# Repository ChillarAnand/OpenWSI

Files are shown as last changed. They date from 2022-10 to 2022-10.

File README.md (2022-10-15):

### OpenWSI

OpenWSI: a low-cost, high-throughput whole slide imaging system via single-frame autofocusing and open-source hardware

### Description

Recent advancements in whole slide imaging (WSI) have moved pathology closer to digital practice. Existing systems require precise mechanical control and the cost is prohibitive for most individual pathologists. Here we report a low-cost and high-throughput WSI system termed OpenWSI. The reported system is built using off-the-shelf components including a programmable LED array, a photographic lens, and a low-cost computer numerical control (CNC) router. Different from conventional WSI platforms, our system performs real-time single-frame autofocusing using color-multiplexed illumination. For axial positioning control, we perform coarse adjustment using the CNC router and precise adjustment using the ultrasonic motor ring in the photographic lens. By using a 20X objective lens, we show that the OpenWSI system has a resolution of ~0.7 microns. It can acquire whole slide images of a 225-mm^2 region in ~2 mins, with throughput comparable to existing high-end platforms. The reported system offers a turnkey solution to transform the high-end WSI platforms into one that can be made broadly available and utilizable without loss of capacity.

### Source

https://arxiv.org/abs/1912.03446

### Notes

This repo contains resources mentioned in the above paper. This repo is meant for collaboration for implementation.

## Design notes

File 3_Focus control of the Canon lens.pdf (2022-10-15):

## Focus control of Canon lenses

Chengfei Guo, Zichao Bian, Shaowei Jiang, and Guoan Zheng Department of Biomedical Engineering, University of Connecticut, Storrs, Connecticut 06269, USA

Step 1: Tools Preparation [1]
Below are the tools for lens modification.

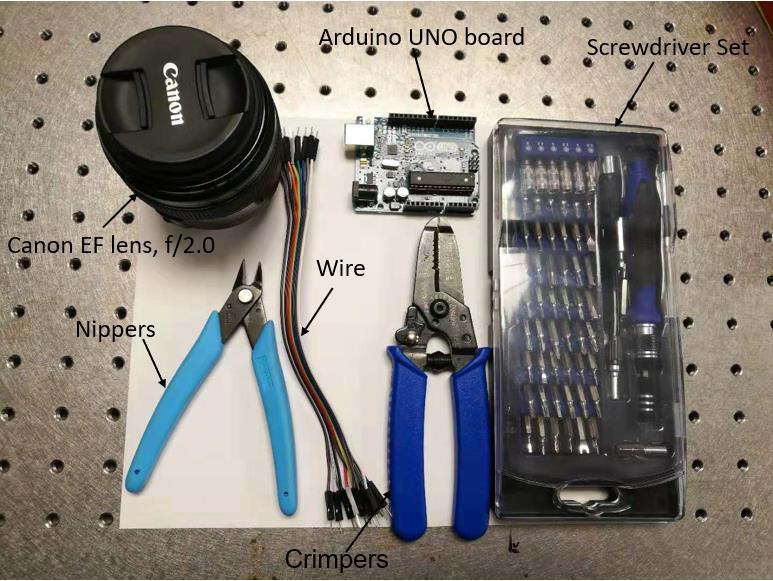
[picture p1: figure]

Figure 1: Tools preparation.

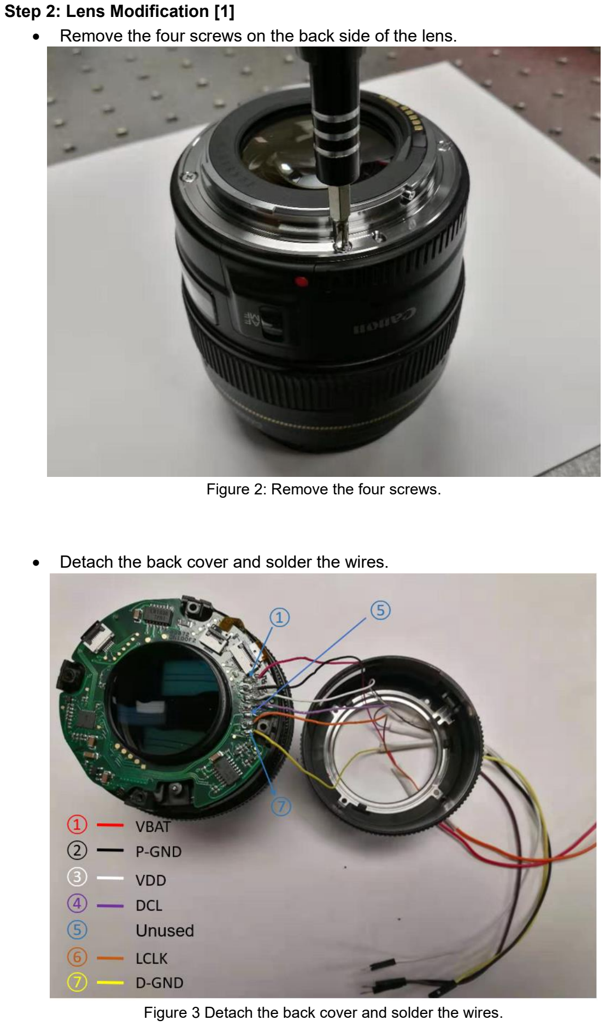
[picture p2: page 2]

Step 2: Lens Modification [1]
- Remove the four screws on the back side of the lens.

Figure 2: Remove the four screws.

- Detach the back cover and solder the wires.

Figure 3 Detach the back cover and solder the wires.

- Reassemble

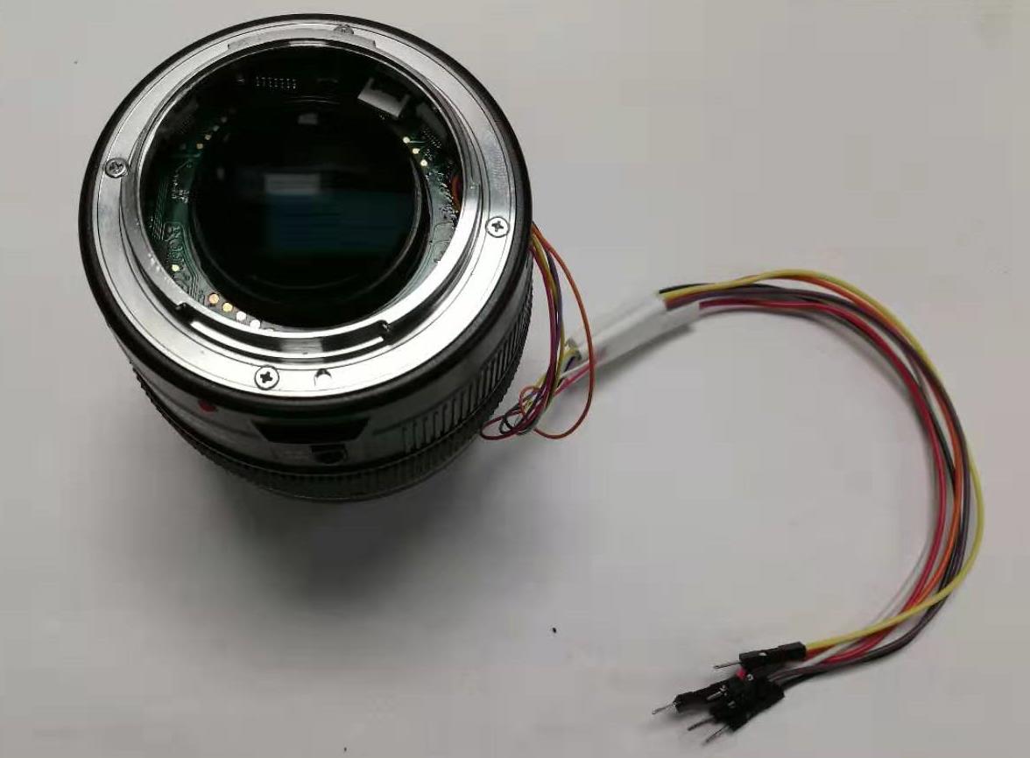
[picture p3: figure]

Figure 4: Reassemble the lens parts.

Step 3: Wire Connection [1]
The lens has motors and control circuits inside and can be connected to an external board via a 7-pin connector. Three pins for the power supply and four pins for a standard SPI interface. We need to wire the pins from outside so that we can send commands from an external board to move the lens ring to the in-focus position. We use an Arduino Uno board (ATmega328P) to perform focus control.
Pin 11 below is defined to send the ‘moving’ command and is connected to the DCL pin of the lens. Pin 13 is used for transferring the clock, which is connected to the CLK pin on the lens. Two GND pins are connected to the D-GND pin and P-GND pin on the lens, respectively. One 5V pin gives power supply for the lens control circuits and is connected to the VDD pin on the lens. We define an output pin as the digital logic high for the power supply of lens motors. The pinout diagram and schematic is listed below.

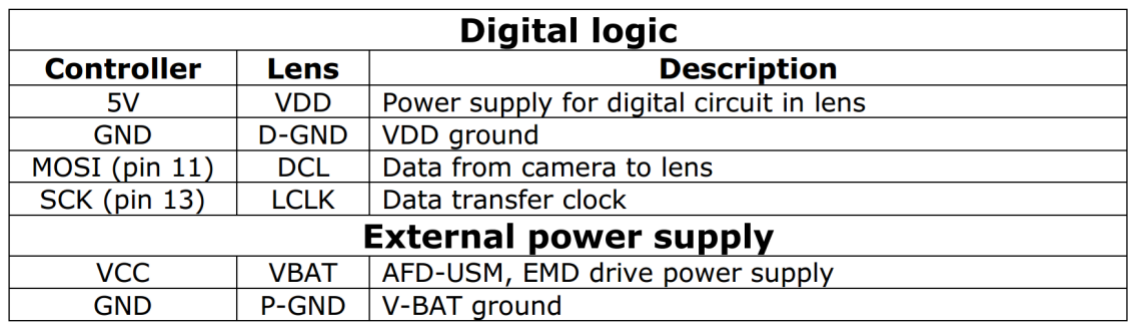
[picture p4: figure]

Figure 5: Pinout diagram.

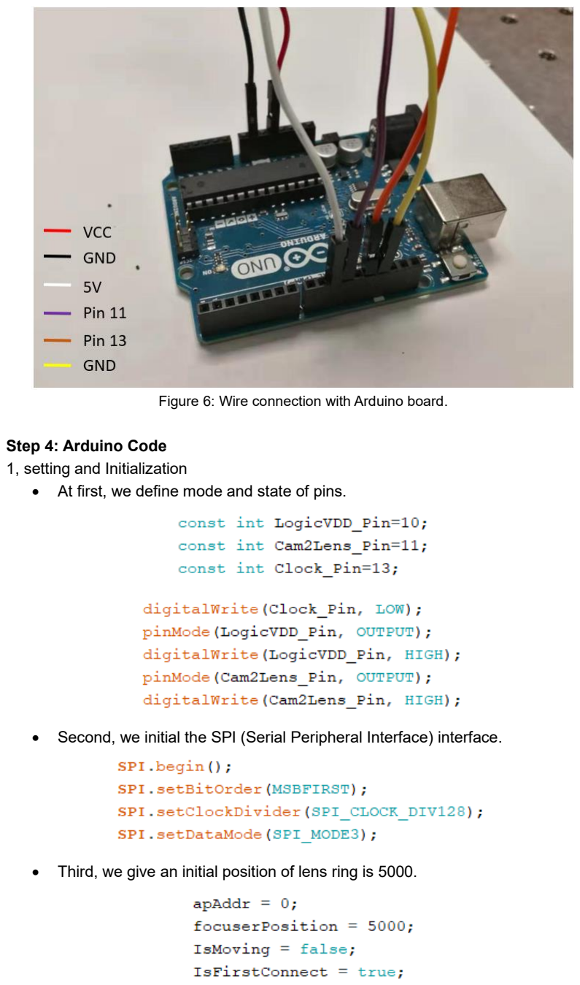
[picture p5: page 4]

Figure 6: Wire connection with Arduino board.

Step 4: Arduino Code
1, setting and Initialization
- At first, we define mode and state of pins.
- Second, we initial the SPI (Serial Peripheral Interface) interface.
- Third, we give an initial position of lens ring is 5000.

- Next, we set the baud rate to 2000000.
- Finally, we initialize the lens.

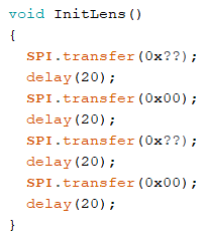
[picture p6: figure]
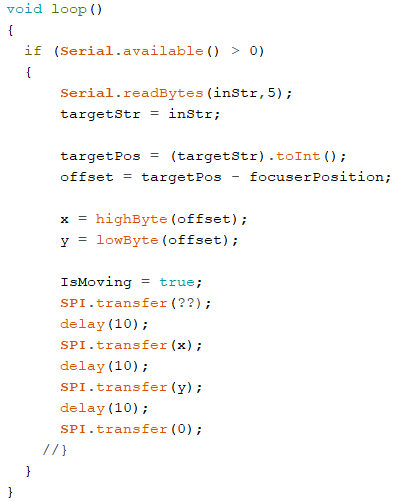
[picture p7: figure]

Note: For the commands of ??, one can email guochengfeii@gmail.com Reference
[1] http://web.media.mit.edu/~bandy/invariant/move_lens.pdf

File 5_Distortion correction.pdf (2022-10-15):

# Digital distortion correction in OpenWSI

We correct the distortion by the following steps:

First, we use a known binary hole-array mask as the sample and capture the corresponding brightfield image in Fig. 1.

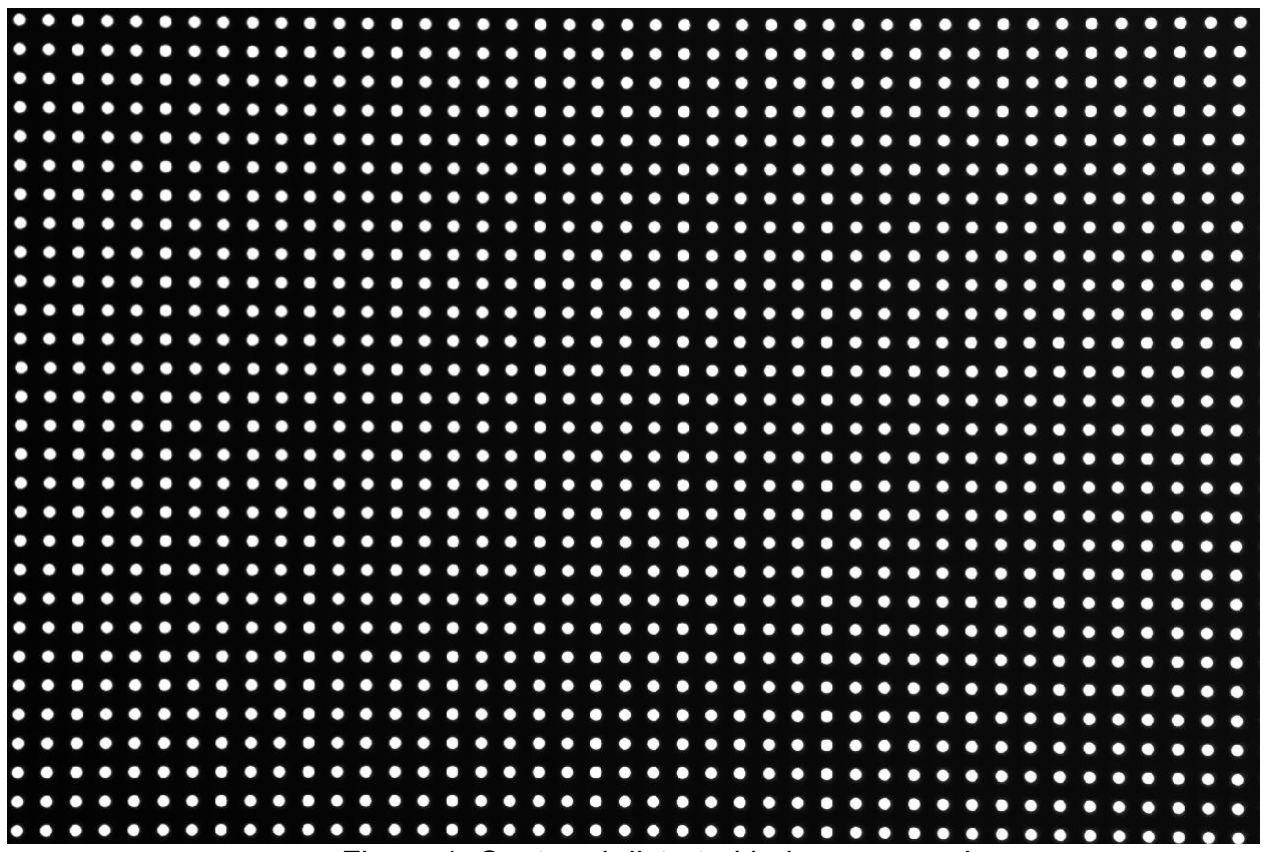
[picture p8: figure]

Figure 1: Captured distorted hole-array mask.

Second, we match the central holes with that of the ground-truth mask. At the edge of the captured hole array image, we can see the position mismatch between the ground-truth mask and the captured image, as shown in Fig. 2(a).

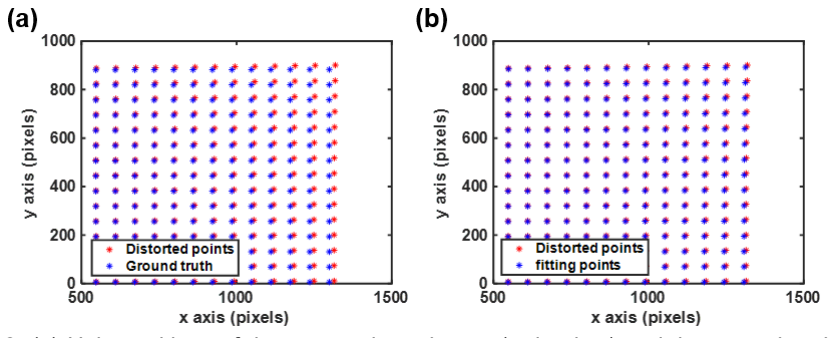
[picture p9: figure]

Figure 2: (a) Hole positions of the captured raw image (red points) and the ground-truth mask (blue points). (b) Hole positions of the captured image after the fitting process.

Third, we fit the distorted hole-positions using those of ground-truth hole positions:

xdistort = x(1 + k1

(x

2 + y

2
) + k2(x

2 + y

2
)

2
)

ydistort = y(1 + k1

(x

2 + y

2
) + k2(x

2 + y

2
)

2
)

where x and y are the ground-truth pairs, xdistort and ydistort are the distorted pairs, k1 and k2 are the coefficients for calibration. In Fig. 2(b), we can see that the fitted hole positions are well aligned with the positions of the ground truth mask.

Fourth, we apply the coefficients to correct the distortion of the raw captured images. We correct the distortion of all tiles we captured. For each image, the processing time is ~0.13 seconds. In Fig. 3, we show the stitching performance with and without the reported distortion correction process. We can see that there are no stitching artifacts after performing distortion correction. The demo code can be found in ‘Demo code’.

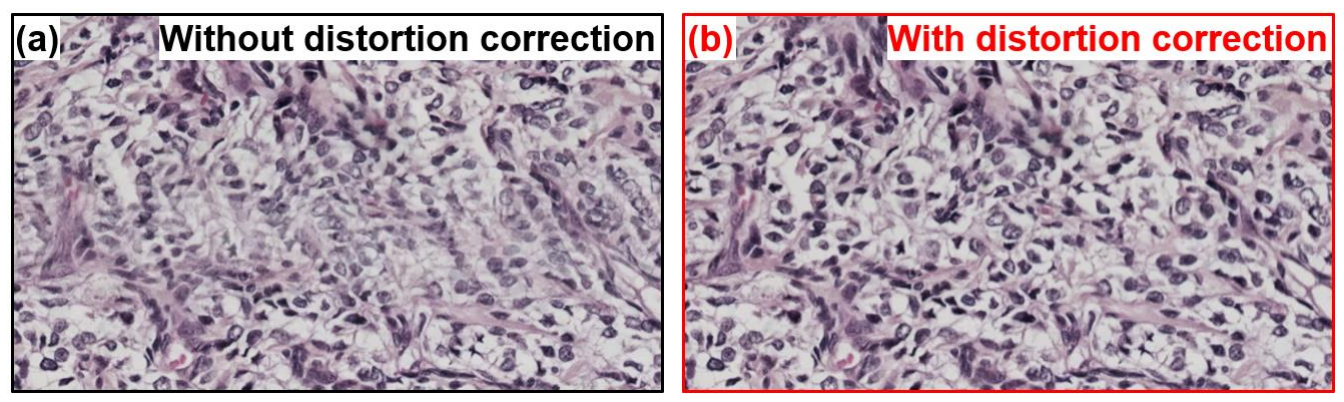
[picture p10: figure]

Fig. 3. Stitching performance without (a) and with (b) distortion correction.

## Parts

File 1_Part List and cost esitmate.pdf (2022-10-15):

## Table 1 Part list and estimated cost for the OpenWSI system

| Item | Specification | Amount | Cost (Unit) | Company
Standard Part | Aluminum Breadboard | MB12 12" x 12" x 1/2" | 1 | $151.0 | Thorlabs
| Optical Posts | TR2 Ø1/2", L = 2" | 5 | $5.19 | Thorlabs
| Post Holders | UPH2 Ø1/2", L = 2" | 1 | $32.04 | Thorlabs
| Lens Tube Slip Rings | SM2RC Ø2.20" | 1 | $30.99 | Thorlabs
| Kinematic Mount | KC1-T | 1 | $97.45 | Thorlabs
| Microscope Slide Clips | SLH1 | 1 | $44.39 | Thorlabs
| Camera | DFK 33UX183 | 1 | $675.0 | The Imaging Source
| Camera Lens | Canon EF -100mm - f/2.0 | 1 | $499.0 | Amazon
| Base | MYSWEETY DIY CNC Engraving Machine | 1 | $169.89 | Amazon
| Ball Bearings | LMK8UU Square Ball Bearings, 25 x 25 x 24 mm | 4 | $6.51 | Amazon
| Arduino Board | Arduino UNO, ATmega328P | 1 | $14.99 | Amazon
| Objective Lens | Plan Apo 20x 0.75, DIC N2, ∞/0.17 | 1 | $250 (used) | eBay
| LED | DotStar 8x8 Grid, RGB LED Matrix | 1 | $24.95 | Adafruit
Custom-made | Sorbothane Sheet | SB12C 5" x 2" x 1/2" | 2 | $8.0 | Thorlabs
| Aluminum Extrusion 20 x 40mm | 20 x 40 x 100 mm | 1 | $14.4 | Amazon
| Aluminum Extrusion 20 x 100mm | 20 x 100 x 180 mm | 1 | $3.0 | Amazon
| Slide Holder | Acrylic sheet, 1/4", 152 x 94.6mm | 1 | $2.5 | Amazon
| Z-Stage Board | Acrylic sheet, 1/4", 100 x 46 mm | 2 | $0.75 | Amazon
| Objective Lens Holder | 80 x 75 x 12 mm | 1 | $0.4 | 3D Printed
| Z-Stage Motor Holder | 100 x 42 x 7 mm | 1 | $0.4 | 3D Printed
| LED Holder_1 | 100 x 152 x 4 mm | 1 | $0.4 | 3D Printed
| LED Holder_2 | 34.4 x 36 x 5 mm | 1 | $0.2 | 3D Printed

Right -Angle Bracket 1 | 28 x 28 x 3 mm | 4 | $0.2 | 3D Printed
Right -Angle Bracket 2 | 33 x 28 x 3 mm | 4 | $0.2 | 3D Printed
Right -Angle Bracket 3 | 40 x 21.7 x 4 mm | 2 | $0.2 | 3D Printed
Right -Angle Bracket 4 | 40 x 21.7 x 4 mm | 2 | $0.2 | 3D Printed
| | Total | $ 2083.3

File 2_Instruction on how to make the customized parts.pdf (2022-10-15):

## Instruction on how to make the customized parts

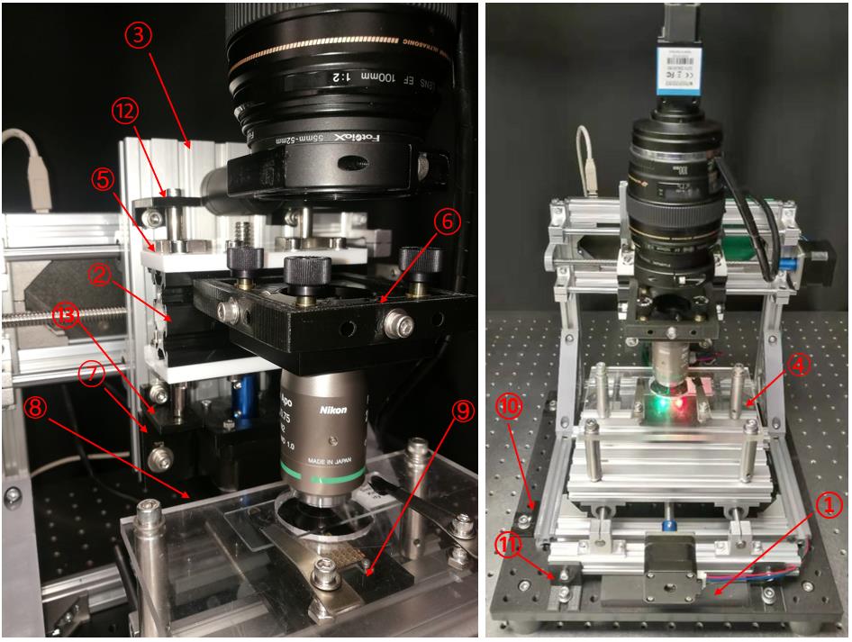
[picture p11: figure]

Figure 1 The custom parts in our prototype

Table 1 List of custom parts
① | Sorbothane Sheet | SB12C 5" x 2" x 1/2" | 2 | $8.0 | Thorlabs
② | Aluminum Extrusion 20 x 40mm | 20 x 40 x 100 mm | 1 | $14.4 | Amazon
③ | Aluminum Extrusion 20 x 100mm | 20 x 100 x 180 mm | 1 | $3.0 | Amazon
④ | Slide Holder | Acrylic sheet, 1/4", 152 x 94.6 mm | 1 | $2.5 | Amazon
⑤ | Z-Stage Board | Acrylic sheet, 1/4", 100 x 46 mm | 2 | $0.75 | Amazon
⑥ | Objective Lens Holder | 80 x 75 x 12 mm | 1 | $0.4 | 3D Printed
⑦ | Z-Stage Motor Holder | 100 x 42 x 7 mm | 1 | $0.4 | 3D Printed

⑧ | LED Holder_1 | 100 x 152 x 4 mm | 1 | $0.4 | 3D Printed
⑨ | LED Holder_2 | 34.4 x 36 x 5 mm | 1 | $0.2 | 3D Printed
⑩ | Right-Angle Bracket 1 | 28 x 28 x 3 mm | 4 | $0.2 | 3D Printed
⑪ | Right-Angle Bracket 2 | 33 x 28 x 3 mm | 4 | $0.2 | 3D Printed
⑫ | Right-Angle Bracket 3 | 40 x 21.7 x 4 mm | 2 | $0.2 | 3D Printed
⑬ | Right-Angle Bracket 4 | 40 x 21.7 x 4 mm | 2 | $0.2 | 3D Printed

## Comments:

①: This one can be bought from the online store of Thorlabs. The part number is SB12C. The original size is 12" x 12" x 1/2", and we need to cut it to the size of 5" x 2" x 1/2" for our use.

②-③: The two elements can be bought from Amazon. We need to cut them to the size of 20 x 40 x 100mm and 20 x 100 x 180mm.

④-⑤: The two elements can be bought from Amazon. We need to drill some holes for screws. We design the sketches in solidworks and create a 3D model. We then use a milling machine (Roland, SRM-20) to make the holes. The 2D sketches are listed below.

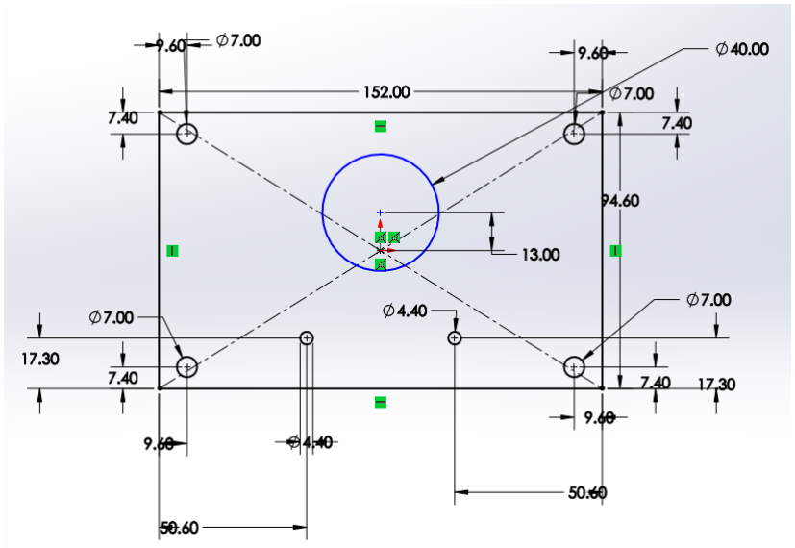
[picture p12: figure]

Figure 2: The sketch of the slide holder. Unit: mm

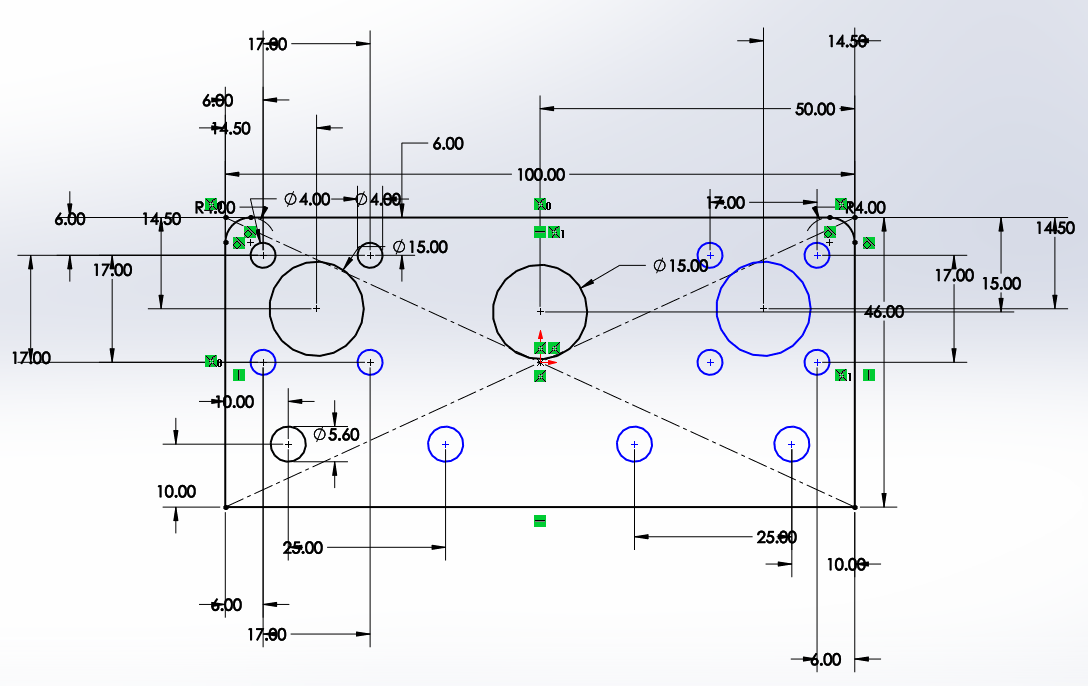
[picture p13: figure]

Figure 3: The sketch of the z-stage holder. Unit: mm

⑥-⑬: These elements are 3-D printed. The machine we used is MakerBot Replicator 2 Desktop 3D Printer. We also provide the Solidworks model in ‘3D design files’.

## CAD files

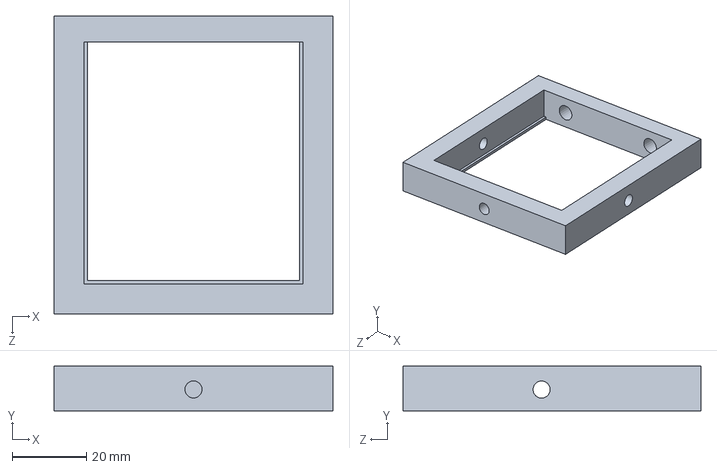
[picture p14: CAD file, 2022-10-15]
6_3D design files/3D-printed solidworks model/Objective Lens Holder.SLDPRT
75.0 x 12.0 x 80.0 mm

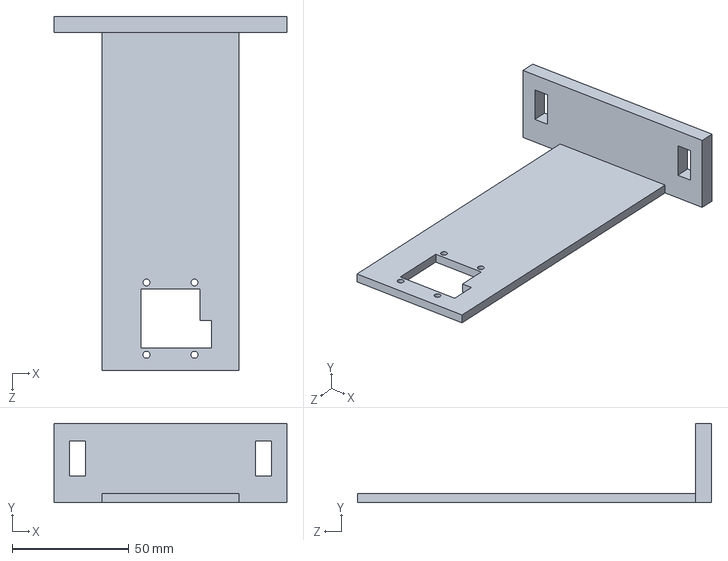
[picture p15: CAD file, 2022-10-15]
6_3D design files/3D-printed solidworks model/LED Holder_1.SLDPRT
100.0 x 34.0 x 152.0 mm

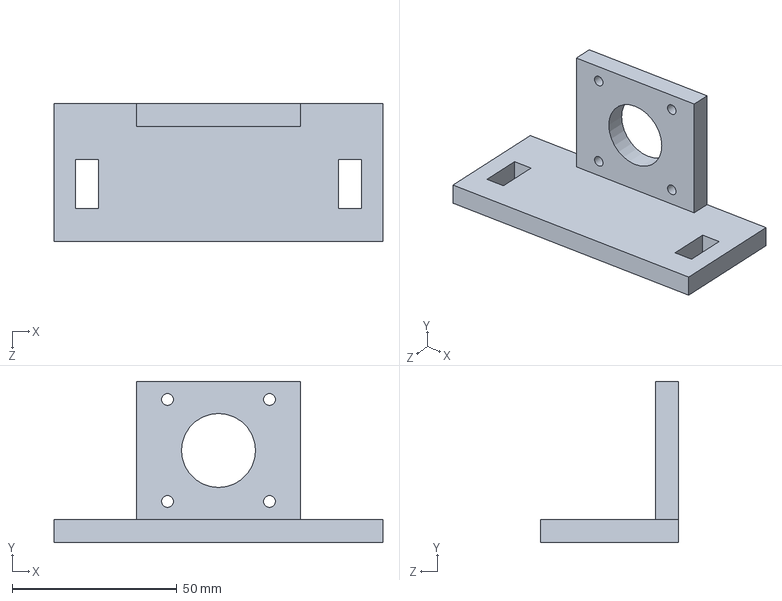
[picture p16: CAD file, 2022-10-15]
6_3D design files/3D-printed solidworks model/Z-Stage Motor Holder.SLDPRT
100.0 x 49.0 x 42.0 mm

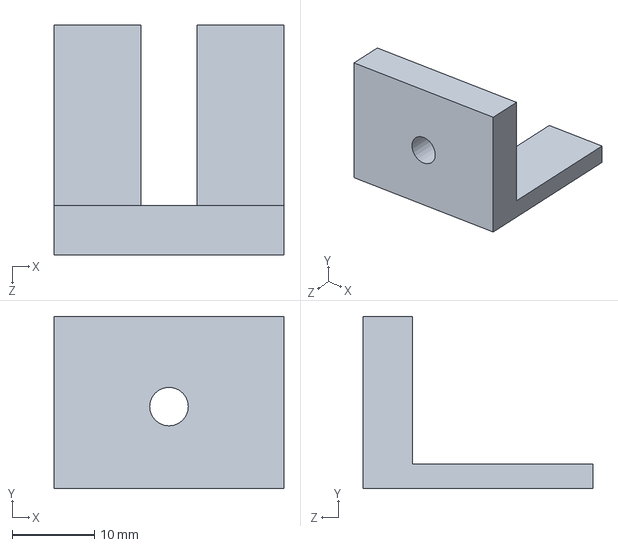
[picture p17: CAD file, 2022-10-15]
6_3D design files/3D-printed solidworks model/Right-Angle Bracket 1.SLDPRT
28.0 x 21.0 x 28.0 mm

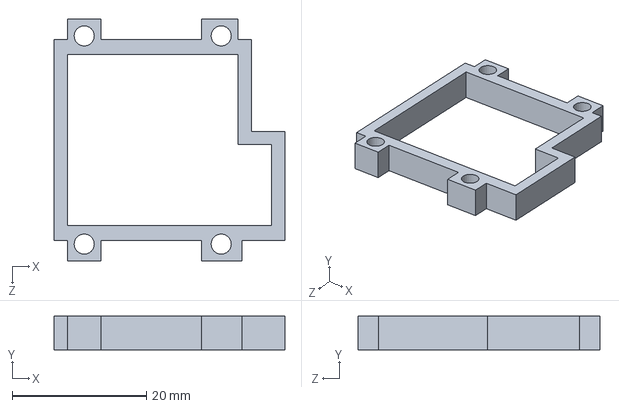
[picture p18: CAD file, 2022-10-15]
6_3D design files/3D-printed solidworks model/LED Holder_2.SLDPRT
34.4 x 5.00 x 36.0 mm

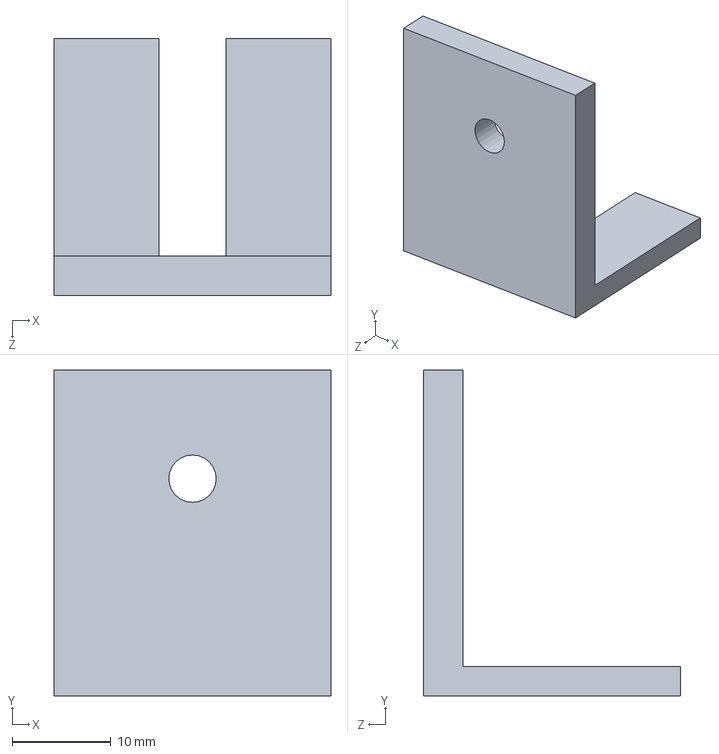
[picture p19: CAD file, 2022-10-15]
6_3D design files/3D-printed solidworks model/Right-Angle Bracket 2.SLDPRT
28.0 x 33.0 x 26.0 mm

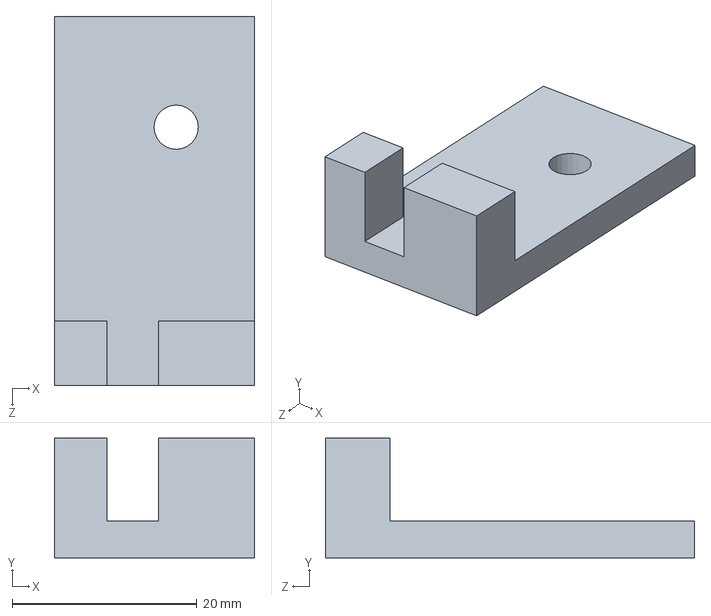
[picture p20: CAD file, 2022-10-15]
6_3D design files/3D-printed solidworks model/Right-Angle Bracket 3.SLDPRT
21.7 x 13.0 x 40.0 mm

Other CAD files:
6_3D design files/3D-printed solidworks model/Right-Angle Bracket 4.SLDPRT

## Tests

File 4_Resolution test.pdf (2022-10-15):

## Resolution of the prototype platform

We captured an image of the USAF resolution target to validate the resolution performance of the reported prototype platform. As is shown in Fig. 1, we can resolve 0.35-µm half-pitch linewidth in group 10, element 4, corresponding to a resolution of ~0.7 µm.

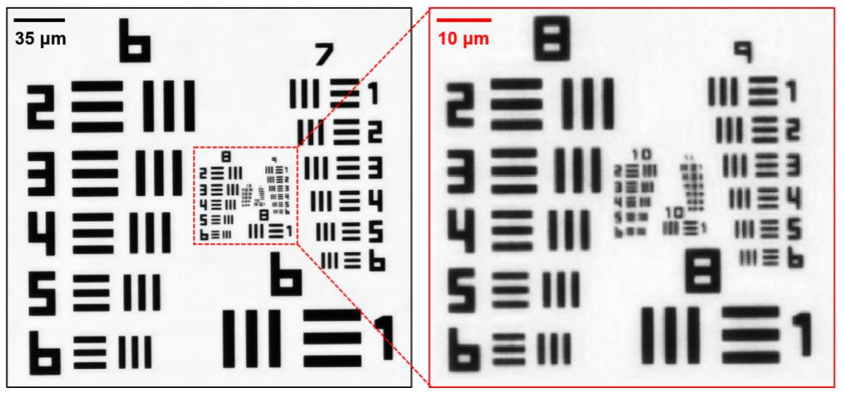
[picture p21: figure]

Figure 1: Resolution test of the reported OpenWSI prototype platform.
